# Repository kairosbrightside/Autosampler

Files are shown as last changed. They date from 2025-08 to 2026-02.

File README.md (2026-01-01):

# Introduction
This repository contains the code and documentation for L.U.N.A. (Laboratory/Low-cost Unit for Near-background Autosampling), a custom-built autosampler designed to collect air samples at remote locations. L.U.N.A. uses a CR3000 micrologger to control valves and a pump, as well as to interface with a pressure sensor. Samples are collected in 0.8 L SUMMA canisters; LUNA uses derivative-based fill termination to determine when the pump has reached its limit. Logged data is stored in a CompactFlash card for later analysis.

# Hardware
### Electrical
- CR3000 micrologger (Campbell Scientific)
- Pump (??? has no identifying markings but it runs on 12V!)
- Digital pressure gauge (MCMaster Carr)
- Songle relays (generic), using an 8-relay board for 7 valves + pump and inlet valve
- Terminal voltage board 8 x 2 (generic) for distributing 12V to pump and valves
- RS232-USB connector for connecting laptop to export data and upload script (it is picky about cables though)
- Power supply for CR3000 (18V DC from 120V AC wall voltage adapter)

##### Schematic showing pin connections


### Gas Flow
- Magnesium perchlorate ${\rm Mg(ClO}_4{\rm )}_2$ tube (homemade)
- 8x electronically actuated valves (US Solid)
    - 6x valves for samples
    - 1x vent valve
    - 1x inlet valve (to keep ${\rm Mg(ClO}_4{\rm )}_2$ dry)
- 6x sample cans (0.8 L SUMMA)
- 3x Swage cross
- 1x Swage tee
- 1x bulkhead fitting for inlet
- 1/4 in stainless steel tubing to construct manifold. I am not sure how much I ended up using, sorry
- 1/4 in Synflex tubing 

# Purpose of the program
### Control pump and valves 
- Pump control: turn pump on and off
- Valve control: open and close NC valves. The sampling valve and pump can activate at the same time, but the valve should close before the pump does. The valve I am currently using is a US Solid motorized ball valve that takes a couple seconds to open or close, so I will have to experiment with the timing there
-  Purge the line for 5 minutes before opening the can
- The pump and valves are using songle relays for activation. The sample valves are on C1-6, the purge valve is on C7, and the pump and inlet valve are on C8 of the CR3000
  
### Read pressure sensor
- The CR3000 is using a 1s scan rate
- The pressure sensor covers a range of 0 to 145 psig. The recorded pressure is then converted to a voltage between 1 and 4 V, so a function is created for pressure readout such that:
  
$$ y = \frac{145}{4}(x-1) $$

where $y$ is the pressure and $x$ is the output voltage. The output is read through the CR3000's first analog channel.

**wiring note:** DC+ should be connected to **brown** and DC- should be connected to **blue**!!

### Stop samples at the limit of the pump
- The program uses an exponential smoothing function to calculate when the pump has hit its limit. This is accomplished by calculating the exponentially smoothed derivative of the pressure, and then stopping when that derivative only deviates by values within the noise threshold of the sensor for several increments in a row.
  
### Sample procedure
1) Open the purge valve (v7) 
2) Turn pump on and run air through sample line for 5 minutes (300 seconds)
3) Close the purge valve and open the valve on a given sample can
4) When $\Delta P \to 0$, open purge valve again. Then vent can and fill again.
5) Once can has been vented 2x, close purge valve and keep can valve open. Fill can.
6) Finally, log final sample pressure and time

### write logged data to CF card
- I think someone still needs to connect their computer to it to actually export the data though... sorry

# Tests before fielding
### 9/15/25 Week-long leak test
On Monday, 9/8, collected 3 samples of roof air 1h apart and held them for a week. On 9/15, removed the samples to measure them. 
Cans 1 and 3, which were at 40.36 and 40.39 psig respectively, maintained their pressures when measured by an analog gauge, but can 2 went down to 31 psi for some reason.

Turning the autosampler on its side to leak-check valve connections did not show any major leaks (at least when checked with Swagelock snoop fluid?). 
However, the source of the large leak after turning off the pump was identified to be the pump itself, as capping the inlet resulted in a significant increase in the time it took for the system to go down from 40 psig, and I felt it with my hand too.
After capping the pump, the leak rate went down to 0.1 psig every 5ish seconds, with the 4 suspect valves (the one whose can failed the leak test and the 3 new ones) open and capped.
Closing these valves resulted in an even faster leak rate of 0.1 psig/3 seconds, which indicates that the majority of the leak is probably within the manifold, and not past one of its valves.

##### 9/8 pressure logs:
```
"TOA5","CR3000","CR3000","3626","CR3000.Std.09","CPU:prototype.CR3","11936","SampleLog"
"TIMESTAMP","RECORD","V_Pressure","Pressure_psi","State","SampleID","CurrentCan","HourNow","MinuteNow"
"2025-09-08 10\:42:57",0,2.113,40.36,"SHUTDOWN",1,1,10,42
"2025-09-08 11\:42:57",1,2.115,40.41,"SHUTDOWN",2,2,11,42
"2025-09-08 12\:42:57",2,2.114,40.39,"SHUTDOWN",3,3,12,42
```
### 10/15 Balcony Test!
> 1:30 PM: Installation was delayed due to comm issues (broken cables). However, LUNA is finally on the balcony now! Set to take first sample at 2:30.

> 2:30 PM: oops! forgot we were in 24-hour time. Set sample for 3:00 instead `<3`
###### 10/22 pressure logs
```
"TOA5","CR3000","CR3000","3626","CR3000.Std.09","CPU:prototype.CR3","8857","SampleLog"
"TIMESTAMP","RECORD","V_Pressure","Pressure_psi","State","SampleID","CurrentCan","HourNow","MinuteNow"
"TS","RN","","","","","","",""
"","","Smp","Smp","Smp","Smp","Smp","Smp","Smp"
"2025-10-15 15:13:17",0,2.071,38.81,"SHUTDOWN",1,1,15,13
"2025-10-16 15:13:17",1,1.846,30.68,"SHUTDOWN",2,2,15,13
"2025-10-17 15:13:17",2,1.822,29.81,"SHUTDOWN",3,3,15,13
"2025-10-18 15:13:17",3,1.803,29.12,"SHUTDOWN",4,4,15,13
"2025-10-19 15:13:17",4,1.892,32.35,"SHUTDOWN",5,5,15,13
"2025-10-20 15:13:17",5,1.923,33.47,"SHUTDOWN",6,6,15,13
```
It appears that the derivative stop parameters need to be adjusted. 

> 10/22/25 1:20 PM: retrieved autosampler. Testing sample pressures now!

| Sample | $P_{\rm recorded} $| $P_{\rm measured} $ |
|:-------:|:-----------------:|:-------------------:|
| 1 | 38.81 | 35.0 |
| 2 | 30.68 | 30.0 |
| 3 | 29.81 | 28.5 |
| 4 | 29.12 | 27.8 |
| 5 | 32.35 | 30.5 |
| 6 | 33.47 | 29.9 |

> Changed Mg(ClO$_4$)$_2$. Qualitatively, not much was consumed by the 6 samples, and the shielding appears to have worked!

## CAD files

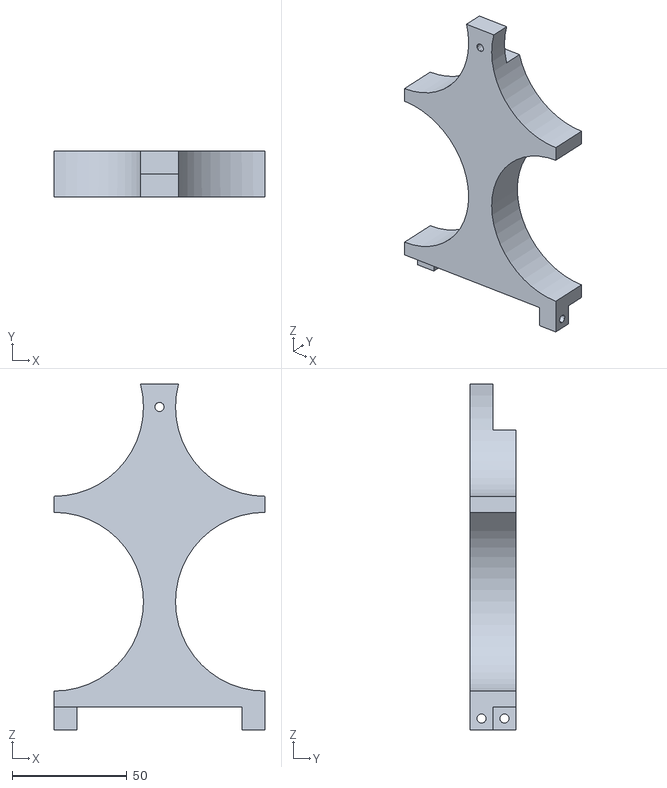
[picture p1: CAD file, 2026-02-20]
gas can holder/gas can holder mid 2.stl
92.0 x 20.0 x 151.0

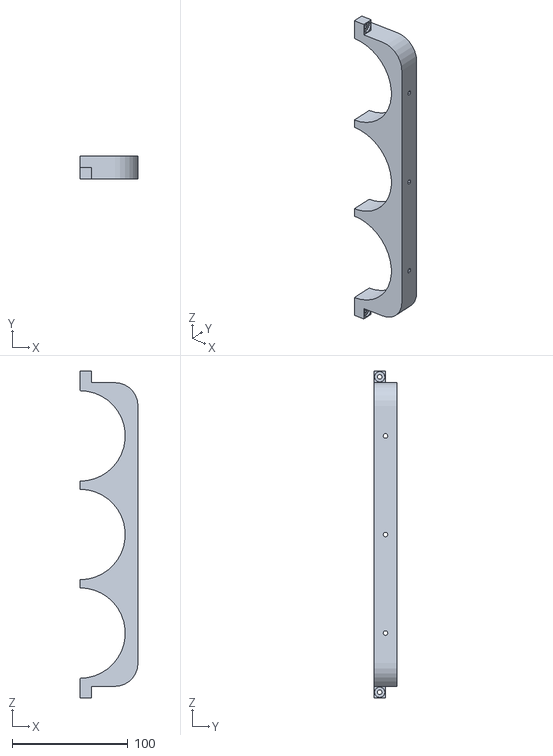
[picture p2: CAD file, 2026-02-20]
gas can holder/gas can holder side.stl
50.0 x 20.0 x 282.0

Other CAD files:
gas can holder/gas can holder mid 1.stl

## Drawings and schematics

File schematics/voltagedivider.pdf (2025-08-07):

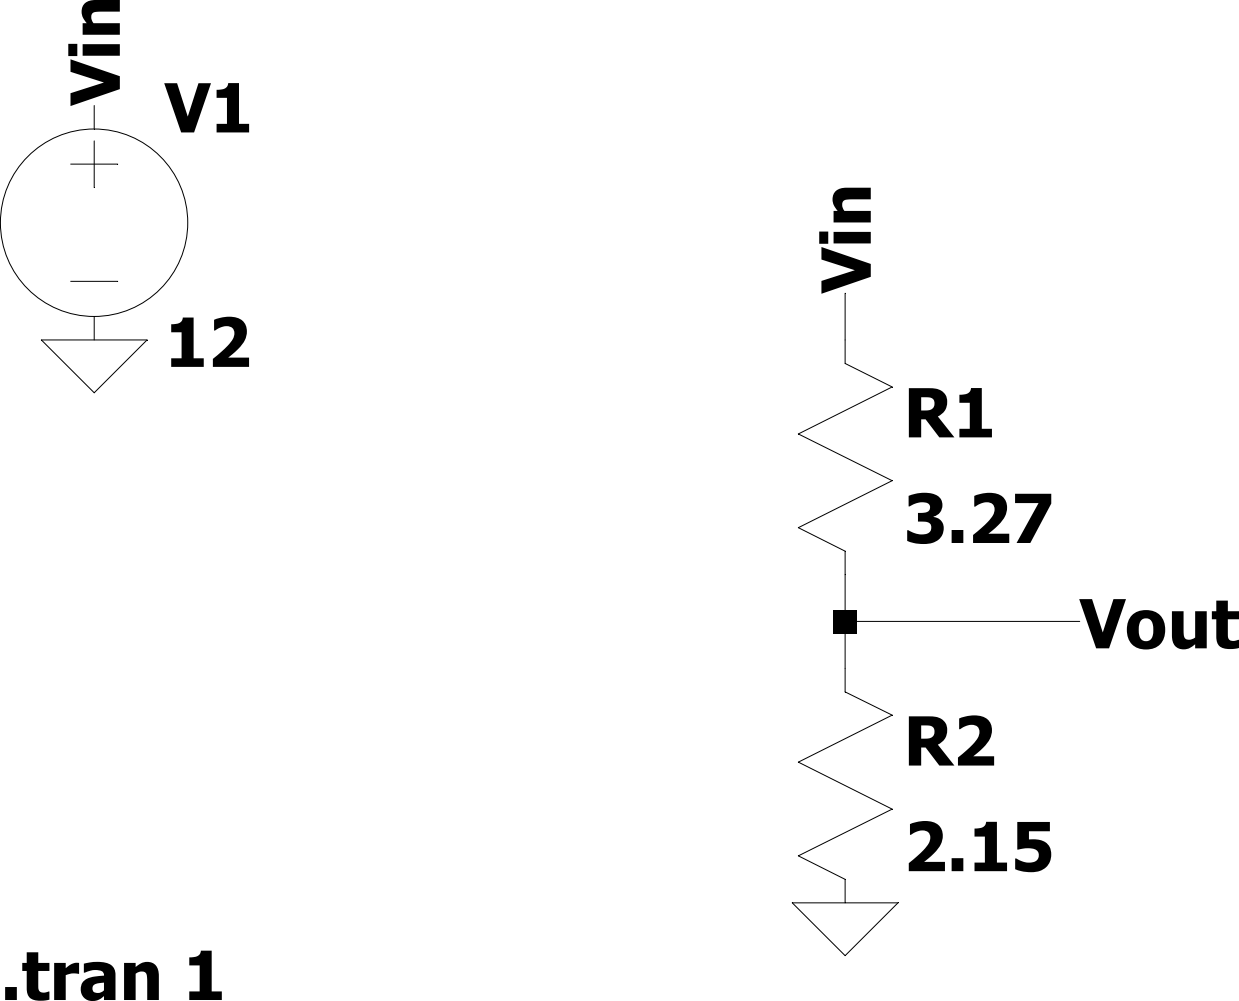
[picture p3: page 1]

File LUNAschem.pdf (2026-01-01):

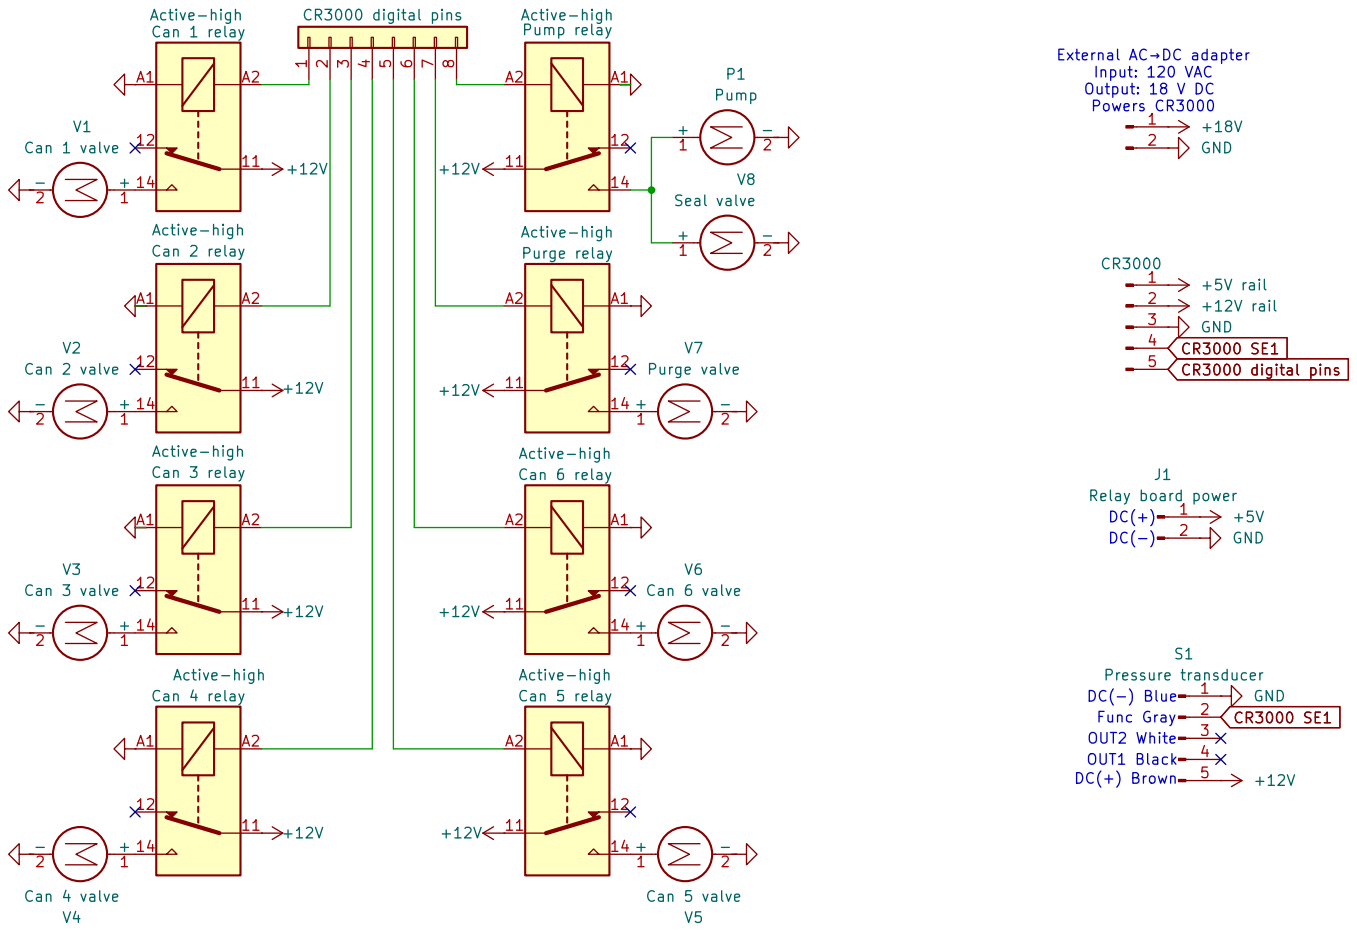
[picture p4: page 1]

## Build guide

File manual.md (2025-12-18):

# L.U.N.A. User Manual
L.U.N.A. (Low-cost Unit for Near-background Atmospheric Samples) is an autonomous air-sampling system designed to collect near-background atmospheric samples into SUMMA canisters with minimal user intervention. 
The system is intended for deployment at semi-remote locations where power is available but frequent manual sampling is impractical.
L.U.N.A. uses a CR3000 micrologger to coordinate valve actuation, pump control, and pressure monitoring. 
Sample termination is determined using the rate of change of pressure, rather than a fixed pressure setpoint, allowing robust operation despite sampling condition variability.

### System Capabilities
- Autonomous daily sampling at scheduled times
- Sequential filling of up to 6 SUMMA canisters
- Line purge prior to sampling
- Multiple can purge/vent cycles before final fill
- Derivative-based fill termination (pump-limited)
- Event-based logging to CompactFlash 

### Hardware 
#### Electrical Components
| Component                                    | Purpose                  | Notes                                      | Failure Risk                         |
| -------------------------------------------- | ------------------------ | ------------------------------------------ | ------------------------------------ |
| **CR3000 Micrologger** (Campbell Scientific) | System controller        | Runs CRBasic program, handles timing & I/O | Low                                  |
| **Songle Relay Board (8-channel)**           | Switches pump and valves | cheap, replaceable                         | **High** (most likely failure point) |
| **US Solid Motorized Ball Valves**           | Gas flow control         | Normally-closed                            | Low                                  |
| **12 V DC Pump**                             | Pressurizes canisters    | can be switched out if it fails            | Medium                               |
| **Pressure Transducer (McMaster-Carr)**      | Measures can pressure    | 1–5 V analog output                        | Low                                  |
| **Terminal Distribution Block**              | 12 V power distribution  | Passive                                    | Low                                  |
| **18 V DC Power Supply**                     | Powers CR3000            | From 120 V AC                              | Low                                  |

> Honestly if something fails it's probably the relay board, as songle relays are notorious for failing. It's a 5V 8-channel songle relay board

3.2 Gas Flow Components
- Magnesium perchlorate ${\rm Mg(ClO}_4{\rm )}_2$ tube (homemade)
- 8x electronically actuated valves (US Solid)
    - 6x valves for samples
    - 1x vent valve
    - 1x inlet valve (to keep ${\rm Mg(ClO}_4{\rm )}_2$ dry)
- 6x sample cans (0.8 L SUMMA)
- 3x Swage cross
- 1x Swage tee
- 1x bulkhead fitting for inlet
- 1/4 in stainless steel tubing to construct manifold
- 1/4 in Synflex tubing
> The magnesium perchlorate and the sample can connections should be checked carefully. There may come a day where the manifold connection fittings wear out, which means you wil have to find more 1/4" stainless steel tubing and bend it at a 90-degree angle and attach fittings to it and put it on the manifold

### System Design
#### Digital Outputs (CR3000)
| Port  | Function           |
| ----- | ------------------ |
| C1–C6 | Sample can valves  |
| C7    | Purge / vent valve |
| C8    | Pump               |

All relays are active-high (`PortSet = 1` $\to$ `ON`).

#### Analog Inputs
| Channel | Signal                             |
| ------- | ---------------------------------- |
| SE1     | Pressure transducer output (1–5 V) |

Pressure conversion:
$$P_{\rm psi} = \frac{145}{4}(V-1)$$

### Sampling Logic 

L.U.N.A. does not fill to a fixed pressure. Instead, it stops when the smoothed pressure derivative approaches zero, indicating the pump has reached its limit.
This compensates for pump wear, works even if leaks reduce maximum pressure, and avoids false termination due to sensor noise.

### Sampling Sequence
For each canister:

0) Waiting for sample trigger (`State = "WAIT"`)
  - Initializes sampling sequence when a specific time or trigger occurs
1) Line purge (`State = "FIRST_PURGE"`)
  - Purge valve open, pump on
  - Duration: 5 minutes
2) Can purge cycles (`State = "CAN_PURGE"`
  - Can valve open, purge closed
  - Fill until $\Delta P \to 0$
  - Vent can (`State = "VENT"`)
  - Repeat 2x
3) Final fill (`State = "SAMPLE"`)
  - Can valve open
  - Pump runs until derivative-based stop
4) Shutdown (`State = "SHUTDOWN"`)
- Close valves
- Turn pump off
- Log final pressure and timestamp
- Increment sample nummber
- Return system to `WAIT` state

Only one log row per sample is written, as to not be overwhelming.

### Datalogging
- Data stored on CompactFlash card
- Event-based logging (no continuous clutter)
- Exported as CSV via PC400

#### Logged fields:
- Timestamp
- Pressure (V and psi)
- State
- Sample ID
- Can number
- Hour / minute of sample

### Operating the system
#### Startup Checklist
- Verify valves closed
- Verify pump OFF
- Check CF card is inserted
- Confirm CR3000 clock is correct, set to computer clock with PC400 if not
- Confirm COM connection before deployment
- Ensure the sample cans and magnesium perchlorate connections are not leaking
  - It can help to pressurize the system by turning the pump on, setting all the relays to high, and using leak checking fluid to see if there are any bubbles around those connections, or other ones you've changed (keep the cans closed if you do this though!!)

### Deployment
- Power system from wall rails
- Please don't put LUNA in precarious places. I think it could fall down a hill but I don't want to learn....
- Samples collected automatically at scheduled times
  - You can edit the program to change scheduled times if you want. Instructions for this detailed in program comments.

### Troubleshooting Guide
#### Cannot Connect to CR3000 (COM Errors)
Symptoms:
- “serial open failed”
- “unreachable destination”
- PC400 won’t connect

Fixes:
- Check which COM port appears in Device Manager
- Update PC400 station to match that COM port
- Close PC400
- Turn literally everything off and on again
- Get a new RS232-USB cable... It's really picky...
> Disconnecting batteries can cause COM port reassignment.

#### Valves Not Opening / Pump Not Running
> Likely cause: relay failure

Actions:
- Manually toggle relay channels
- Replace Songle relay module if inconsistent

#### Sample Pressure Drops After Collection
> Please note that a small drop ($<5$ psi) in sample pressure after collection is normal, especially if LUNA was put somewhere sunny. This is due to the gas being sampled being at a higher temperature than it will be when it gets to the lab indoors (the sampling area might be hot, and the pump will be hot when the air passes through it)
Possible causes:
- Pump backflow (no check valve)
- Manifold leak
- Valve internal leakage

Diagnostic steps:
- Cap pump inlet and monitor decay
- Close all valves individually
- Leak-check with Swagelok Snoop by opening every valve in the manifold while running the pump0

#### CF Card Not Recording Data
- Ensure CardFlush() is executed after logging
- Confirm card formatted FAT/FAT32
- The CR3000 is picky about what cards it uses, so try a couple different ones
- Check available space
- Try re-inserting card after power cycle

### Maintenance Recommendations
| Component     | Action            | Interval                |
| ------------- | ----------------- | ----------------------- |
| Songle relays | Inspect / replace | As needed               |
| Sample cans   | Leak check        | Before deployment       |
| Drying tube   | Replace Mg(ClO₄)₂ | Before deployment       |
| Valves        | Cycle test        | If acting suspicous     |

### Known Limitations
- Manual data retrieval required
- Songle relays limit lifetime (feel free to replace with another kind of relay, just make sure they're 5V high-active---convenient for the digital pins of the CR3000---or change the program accordingly!!)
- Needs wall power 

### Revision History?0
- v1.0 — Initial field-ready deployment (balcony test)

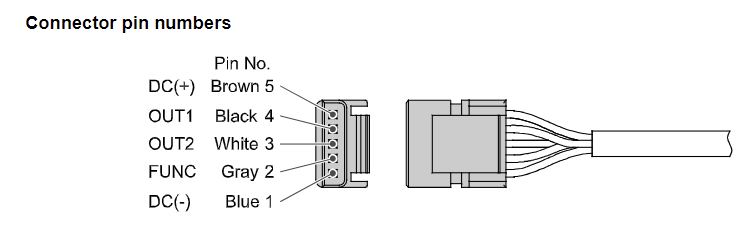
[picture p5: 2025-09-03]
sensorwiring.png

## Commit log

2025-08-04 VoltSE instead of VoltDiff
    sensor wasn't a differential input lol
2025-08-06 added interrupt for when pressure hits threshold
2025-08-07 replaced timeout and ad hoc interrupt with exponential smoothing
    trying to find when rate of change in the pressure is so low it's just noise
2025-08-07 Voltage divider schematic
2025-08-07 turn pump off later
2025-08-08 conditional logging only after sample is taken
    so the data table doesn't fill with random data
2025-09-03 Add files via upload
    Pressure transducer wire colors and meaning
2025-09-06 fixed bug that made currentcan always 3 :(
2025-09-08 Fixed bug that made sampleID always can 3?
    I think if statements also work as for loops in this language for some reason
2025-09-08 currentcan was incrementing every second.. oops. fixed!
2025-12-18 Correct LaTeX syntax in manual.md
    Fix LaTeX formatting for pressure conversion equation.
2026-02-20 Can holder brackets
    Thank you Aurora for designing these!
    [gas can holder mid 1.stl, gas can holder mid 2.stl, gas can holder side.stl]
